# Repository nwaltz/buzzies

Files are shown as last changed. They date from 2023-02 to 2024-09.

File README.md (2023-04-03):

# buzzies
bilateral stimulation tappers for use as a EMDR therapy device through Engineers Without Borders OSU

top level models:

pods: final pod assm.SLDASM

pcb case: pcb assm no snaps.SLDASM

## Production

There are several ways to manufacture the mechanical components needed to house the electrical components for the buzzies.  While the original design concept was produced using a resin SLA printer (Prusa SLIS and Formlabs 3+), components were also designed for injection molding and filament 3D printing.  Each component will have subfolders containing the CAD models, and the subsections below will describe how to manufacture these components.

### Resin SLA Printing

The motivation behind using an SLA printer was to retain the smooth and polished surface finish of an injection molded part while allowing for overhangs and otherwise difficult to manufacture features.  There are four unique parts to manufacture in this design: 4 identical pod halves, a pcb base case, a pcb back cover, and a battery back cover.  

The pod halves are rotationally symmetric about the centerline and will hold a small piezo vibration motor in the center cavity.  Since such motors will generally have small, fragile wires, we recommmend soldering larger (e.g. 16 AWG) wires to the ends of the motor wires.  There is space to house the solder connection within the pods to maintain the strength of the connection. 

Once the motors are soldered and housed within the pods, the pod halves need to be fastened together.  The pod halves will self-align when placed together, and will be fastened with two dowel pins.  There should be two small holes on the side of the pod that the wires exit from.  Insert the dowel pins into these holes to fasten the pods together.  The end of the pin should be flush with the face of the pod.  If the pins seem to be sticking, you may need to lightly tap them with a hammer.

### Injection Molding

### Filament Printing

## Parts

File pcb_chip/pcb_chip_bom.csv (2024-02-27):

Id | Designator | Footprint | Quantity | Comment | JLCPCB Part #?optional? | Column1
1 | U2 | DIP-8_W7.62mm | 1 | IC-8P | C5289485
2 | R6,R5 | R_1206_3216Metric | 2 | rb | C245596
3 | Q1,Q2 | SOT-23 | 2 | TIP41A | C141788
4 | R3,R4 | R_1206_3216Metric | 2 | rm | C237774
5 | C2 | CASE-A-3216 | 1 | 1 uF | C128315
6 | R2 | 805 | 1 | 1k? | C5139712
7 | R1 | R_1206_3216Metric | 1 | 240? | C3017200
10 | C1 | SMD,1.6x3.2mm | 1 | 0.1 uF | C2976899
11 | U1 | SOT-223-3_TabPin2 | 1 | LM317M_SOT-223 | C840113
12 | RV1 |  | 1 | pot | C470307

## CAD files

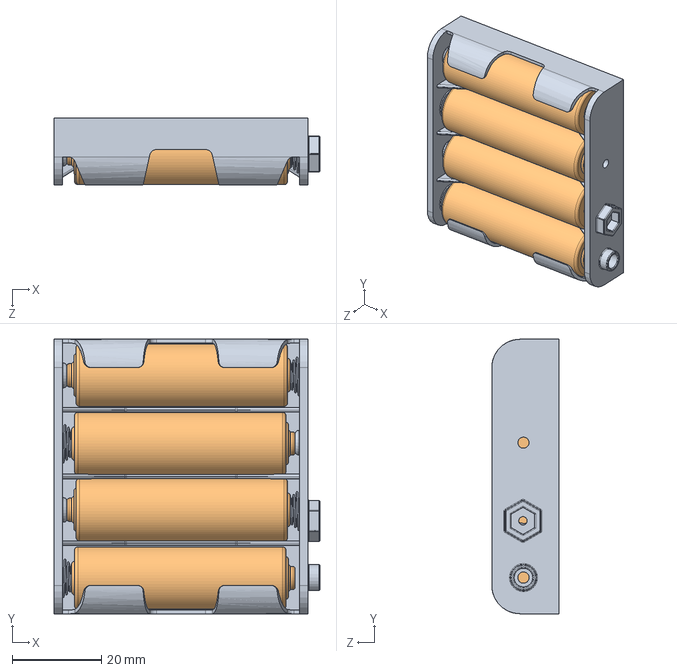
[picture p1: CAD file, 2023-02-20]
pcb assm no snaps/Batterie nel portabatterie.SLDASM
59.6 x 61.5 x 15.1 mm
User Library-R6_AA_UM3-1_5V_holder4AA
Batteria ricaricabile stilo x 4

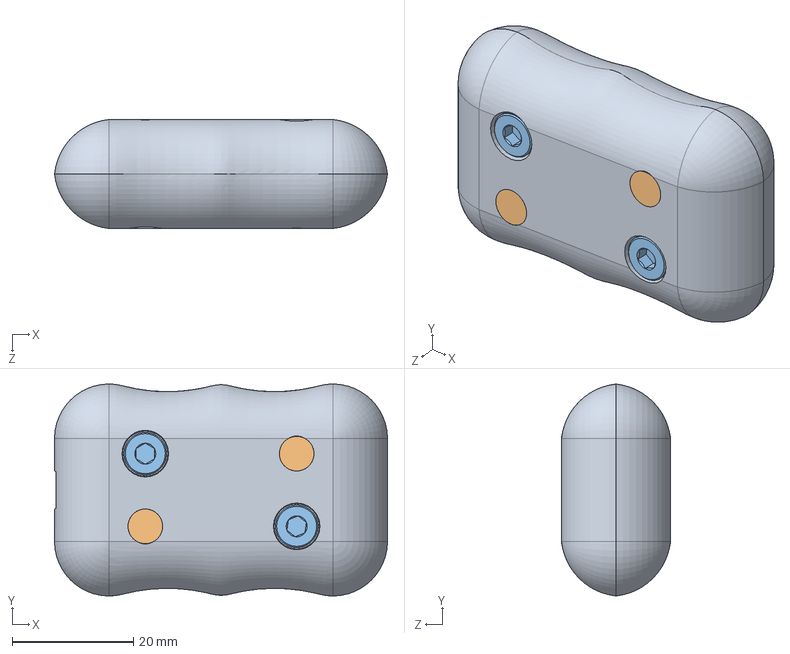
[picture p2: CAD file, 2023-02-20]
final pod assm/final pod assm.SLDASM
55.0 x 35.0 x 18.0 mm
press fit redesign x 2
(INS-PL0008) IBB-M4-4-PennEngineering.stp x 4
91290A148_Alloy Steel Socket Head Screw x 4

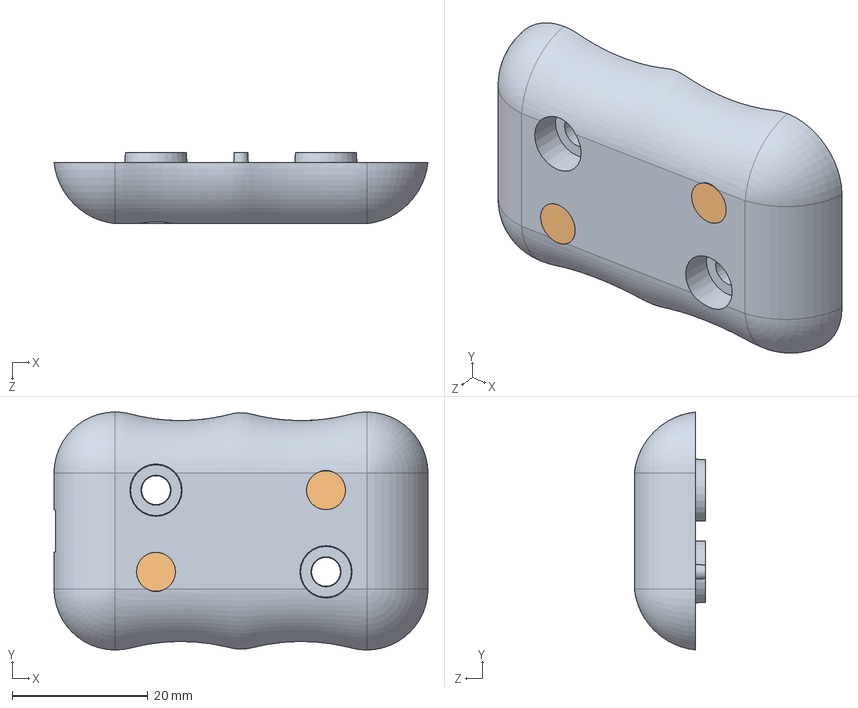
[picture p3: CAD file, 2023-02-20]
final pod assm/press fit assm.SLDASM
55.0 x 35.0 x 10.5 mm
press fit redesign
(INS-PL0008) IBB-M4-4-PennEngineering.stp x 2

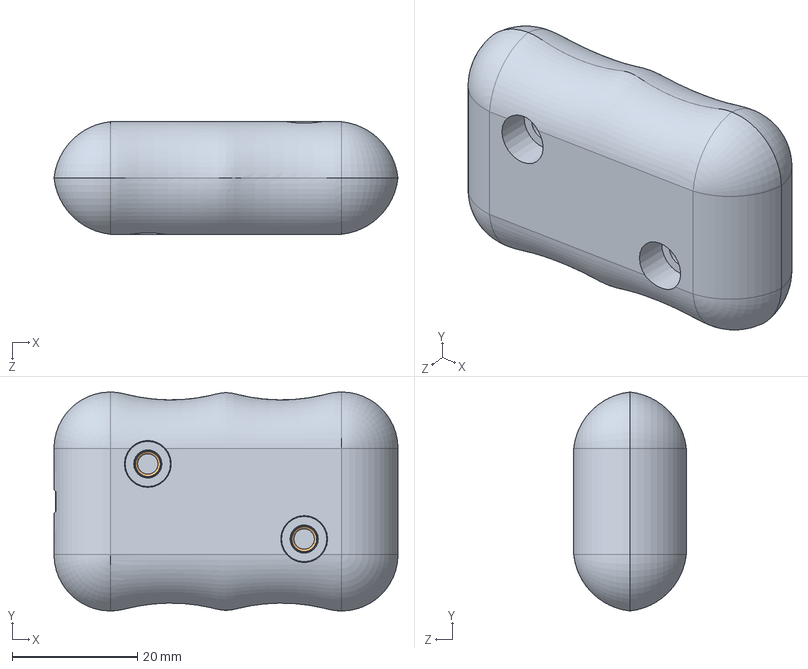
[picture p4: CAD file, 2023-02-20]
final pod assm/pod with inserts test.SLDASM
55.0 x 35.0 x 18.0 mm
snap fit fuck protolabs x 2
(INS-PL0017) STKB-M4-8-PennEngineering.stp x 4

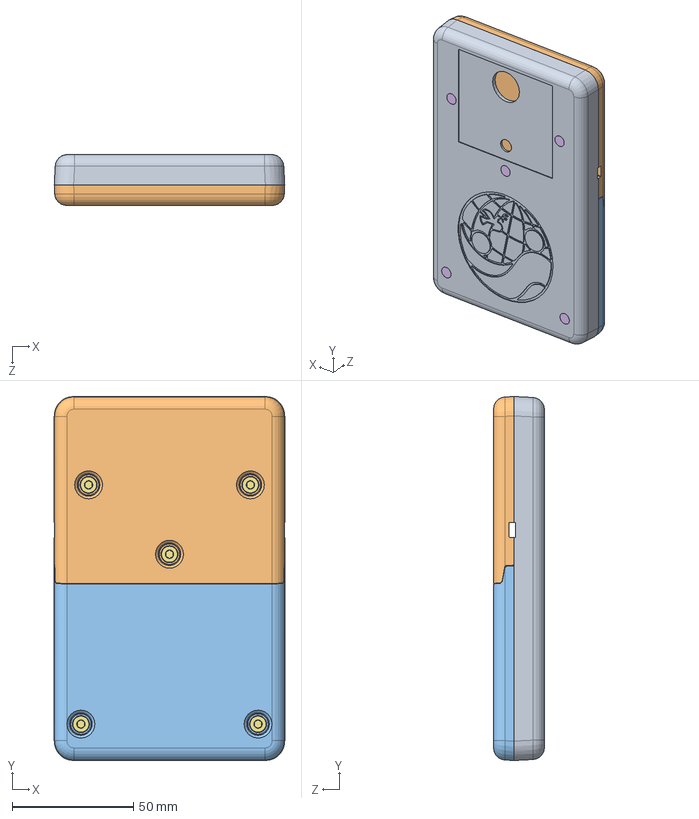
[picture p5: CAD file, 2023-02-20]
pcb assm no snaps/pcb assm no snaps.SLDASM
95.0 x 150.0 x 21.0 mm
pcb top no snaps
pcb bottom no snaps
battery cover no snaps
User Library-R6_AA_UM3-1_5V_holder4AA
Batteria ricaricabile stilo x 4
(INS-PL0008) IBB-M4-4-PennEngineering.stp x 5
91290A148_Alloy Steel Socket Head Screw x 5

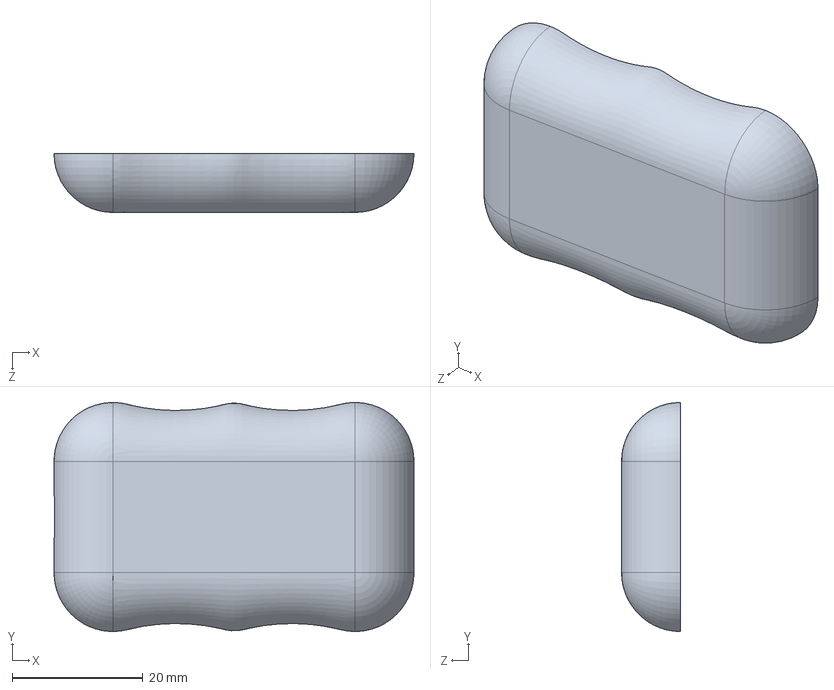
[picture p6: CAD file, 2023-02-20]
final pod assm/pod template.SLDPRT
55.0 x 35.0 x 9.00 mm

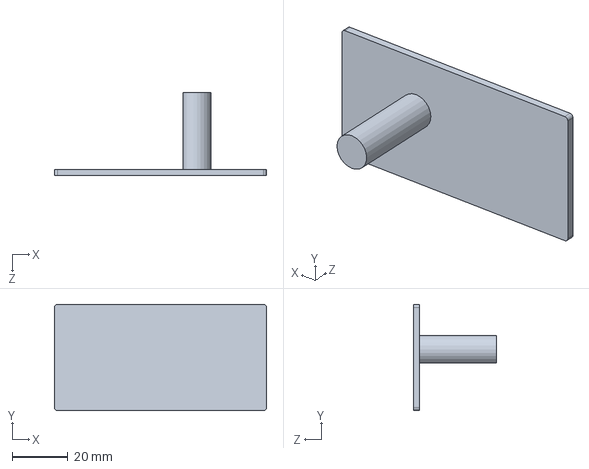
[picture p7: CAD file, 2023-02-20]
pcb assm no snaps/pcb 3x1.5.SLDPRT
76.2 x 38.1 x 30.0 mm

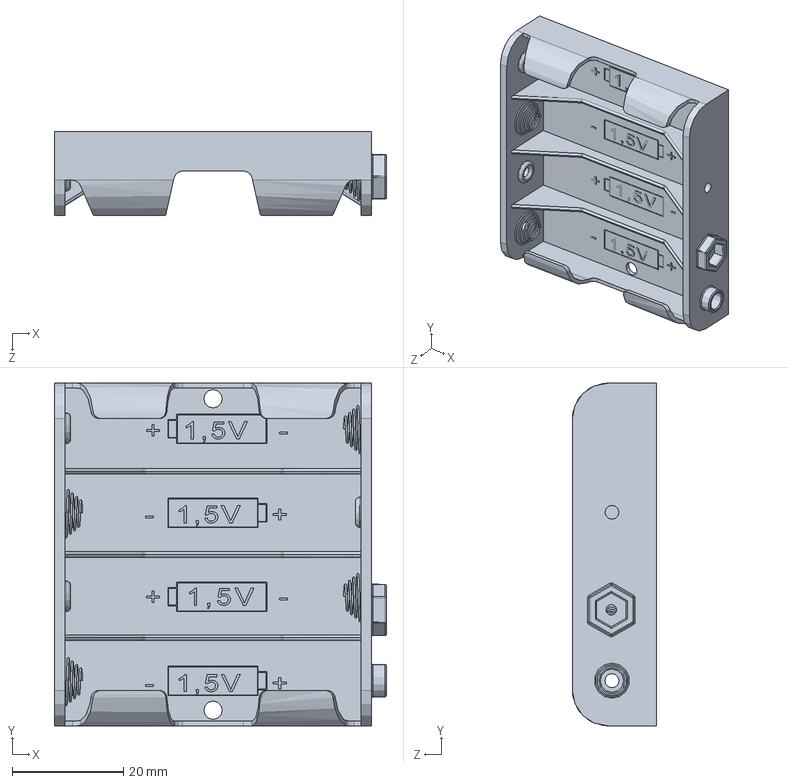
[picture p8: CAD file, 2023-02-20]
pcb assm no snaps/User Library-R6_AA_UM3-1_5V_holder4AA.SLDPRT
59.6 x 61.5 x 15.1 mm

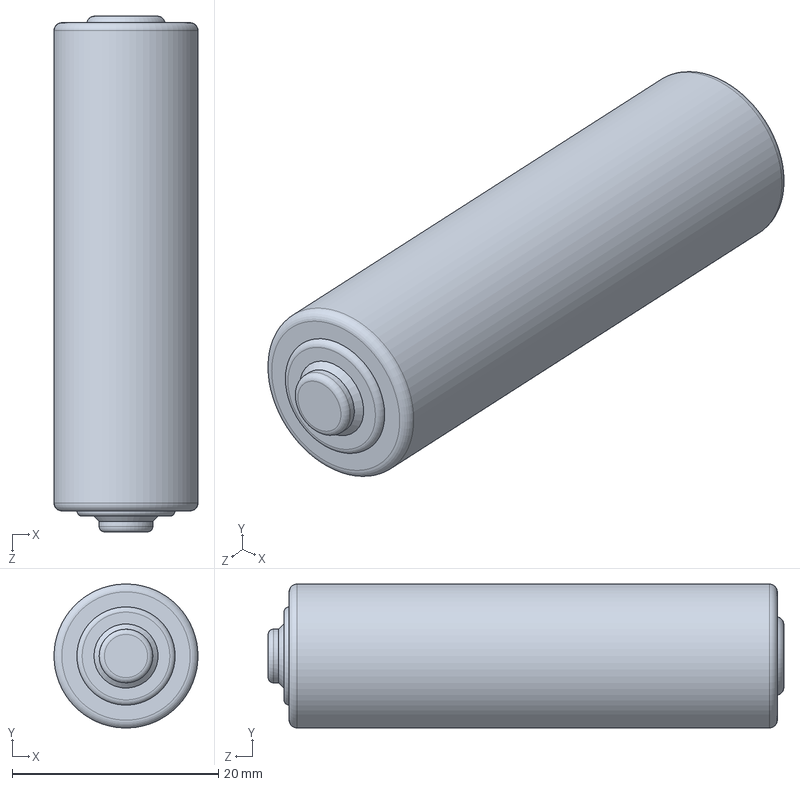
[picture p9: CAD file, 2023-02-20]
pcb assm no snaps/Batteria ricaricabile stilo.SLDPRT
14.0 x 14.0 x 50.0 mm

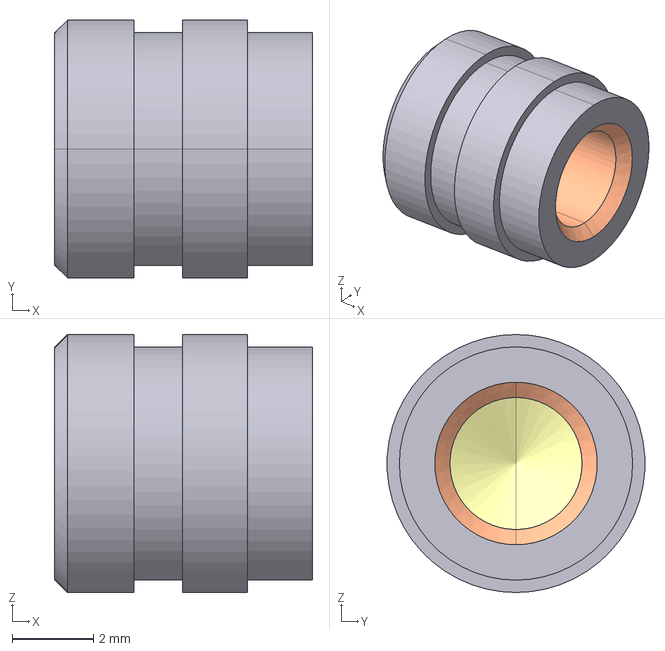
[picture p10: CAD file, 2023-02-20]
final pod assm/(INS-PL0008) IBB-M4-4-PennEngineering.stp
6.35 x 6.34 x 6.35 mm

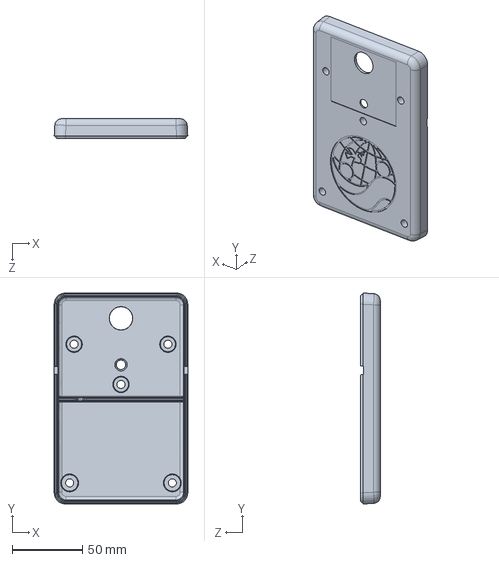
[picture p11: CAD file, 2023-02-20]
pcb assm no snaps/pcb top no snaps.SLDPRT
95.0 x 150.0 x 14.0 mm

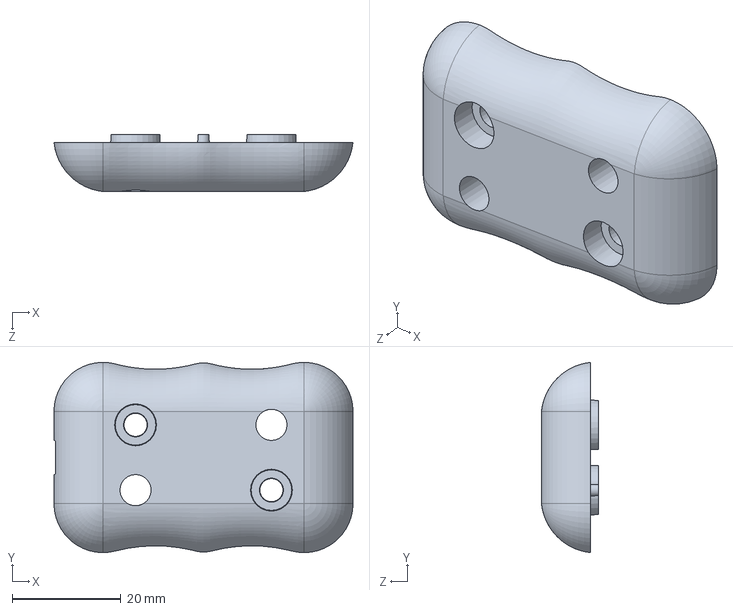
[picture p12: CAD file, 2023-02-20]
final pod assm/press fit redesign.SLDPRT
55.0 x 35.0 x 10.5 mm

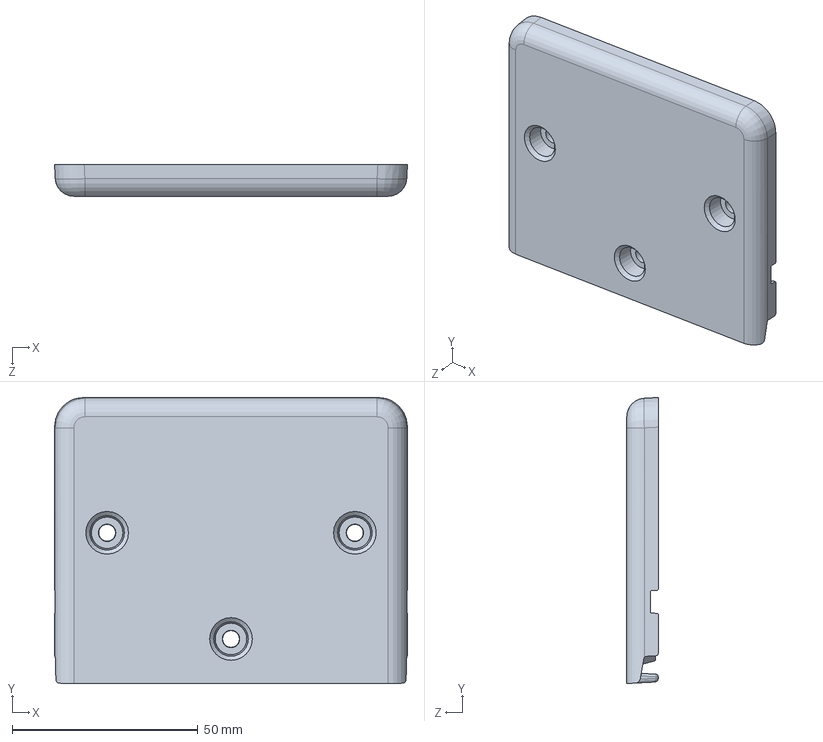
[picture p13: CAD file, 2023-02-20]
pcb assm no snaps/pcb bottom no snaps.SLDPRT
95.0 x 77.0 x 8.50 mm

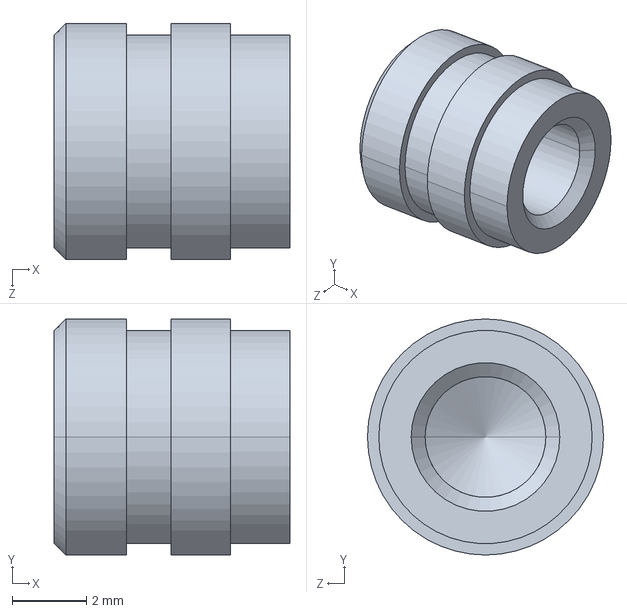
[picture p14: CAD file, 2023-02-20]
final pod assm/(INS-PL0008) IBB-M4-4-PennEngineering.stp.SLDPRT
6.35 x 6.35 x 6.35 mm

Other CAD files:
pcb assm no snaps/battery cover no snaps.SLDPRT
final pod assm/91290A148_Alloy Steel Socket Head Screw.SLDPRT

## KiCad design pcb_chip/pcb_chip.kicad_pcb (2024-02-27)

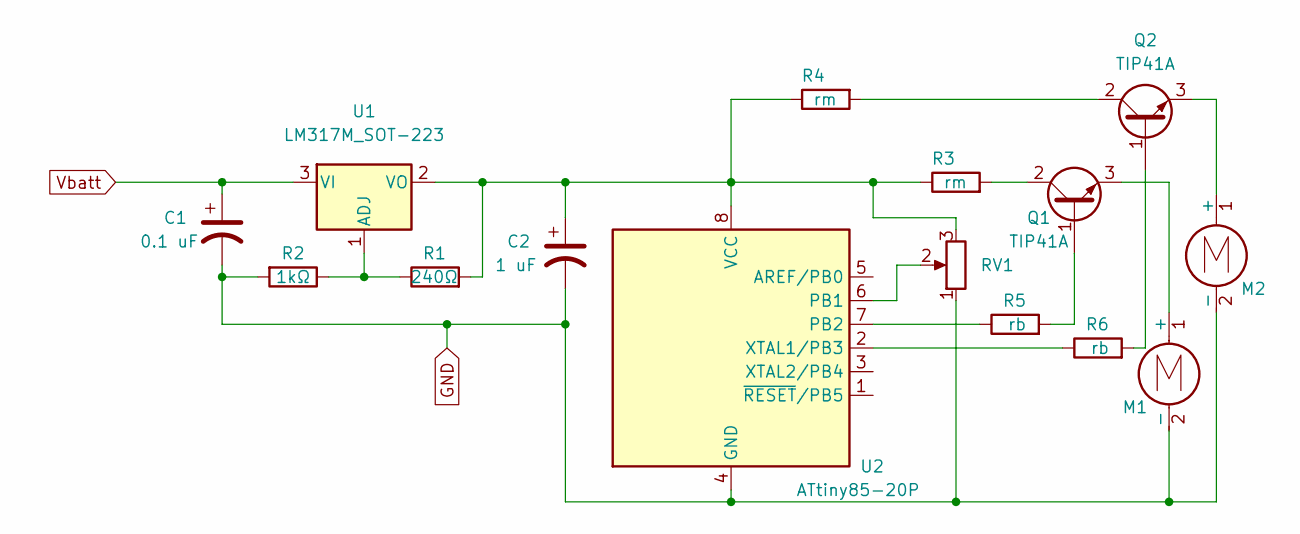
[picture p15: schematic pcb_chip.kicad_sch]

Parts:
C1: 0.1 uF; CP_Elec_4x5.4
C2: 1 uF; CP_Elec_4x5.4
M1, M2: vib_mot; PinHeader_1x02_P2.54mm_Vertical
Q1, Q2: TIP41A; SOT-23
R1: 240Ω; R_1206_3216Metric
R2: 1kΩ; R_1206_3216Metric
R3, R4: rm; R_1206_3216Metric
R5, R6: rb; R_1206_3216Metric
RV1: R_Potentiometer
U1: LM317M_SOT-223; SOT-223-3_TabPin2
U2: ATtiny85-20P; DIP-8_W7.62mm

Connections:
GND: C1.2, C2.2, M1.2 (-), M2.2 (-), R2.2, RV1.1, U2.4 (GND); also elsewhere on the board
unnamed: C2.1, R1.2, R3.1, R4.1, RV1.3, U1.2 (VO), U2.8 (VCC)
unnamed: M1.1 (+), Q1.3 (E)
unnamed: M2.1 (+), Q2.3 (E)
unnamed: R1.1, R2.1, U1.1 (ADJ)
unnamed: Q1.2 (C), R3.2
unnamed: Q2.2 (C), R4.2
unnamed: R5.1, U2.7 (PB2)
unnamed: Q1.1 (B), R5.2
unnamed: R6.1, U2.2 (XTAL1/PB3)
unnamed: Q2.1 (B), R6.2
unnamed: RV1.2, U2.6 (PB1)
Vbatt: C1.1, U1.3 (VI); also elsewhere on the board

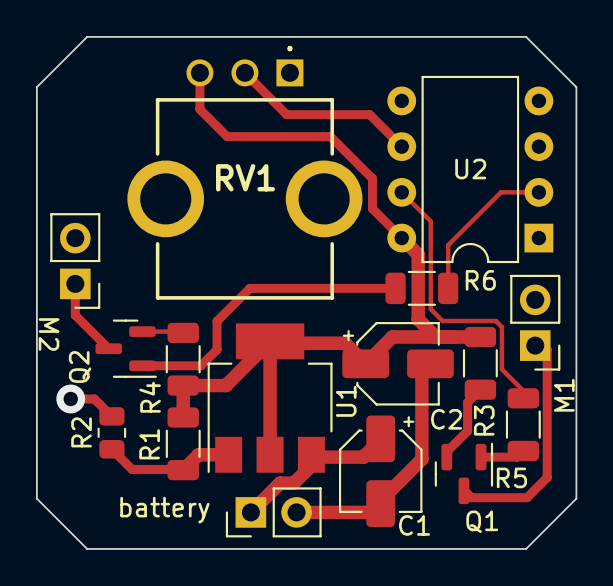
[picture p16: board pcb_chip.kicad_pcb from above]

Board: 2 copper layers, 30.0 x 28.4 mm, 16 parts (0 on the bottom side), 13 nets.

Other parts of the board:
battery: vib_mot; PinHeader_1x02_P2.54mm_Vertical

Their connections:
GND: battery.2 (-); also elsewhere on the board
Vbatt: battery.1 (+); also elsewhere on the board

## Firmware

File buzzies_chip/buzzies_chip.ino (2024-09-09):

int motor_l = 2;
int motor_r = 3;
int pot = 1; // pin 2

int delay_time, analog_in;
int motor_state = 0;
int last_time;

void setup()
{
  pinMode(motor_l, OUTPUT);
  pinMode(motor_r, OUTPUT);
  pinMode(pot, INPUT);
  last_time = millis();
}

void loop()
{
  analog_in = analogRead(pot);
  delay_time = map(analog_in, 0, 1023, 1000, 3000);
  digitalWrite(motor_l, LOW);
  digitalWrite(motor_r, LOW);
  delay(delay_time);
  digitalWrite(motor_l, LOW);
  digitalWrite(motor_r, LOW);
  delay(delay_time);

  
//  if (millis() - last_time > delay_time) {
//    last_time = millis();
//    if (motor_state == 0) {
//      digitalWrite(motor_l, HIGH);
//      digitalWrite(motor_r, LOW);
//      motor_state = 1;
//    }
//    else {
//      digitalWrite(motor_r, HIGH);
//      digitalWrite(motor_l, LOW);
//      motor_state = 0;
//    }
//  }
}

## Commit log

2023-02-20 updated dependencies
    [(INS-PL0008) IBB-M4-4-PennEngineering.stp, (INS-PL0008) IBB-M4-4-PennEngineering.stp.SLDPRT, 91290A148_Alloy Steel Socket Head Screw.SLDPRT, final pod assm.SLD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]
2023-02-20 pod template
    [pod template.SLDPRT]
2024-02-27 added pcb files
    [pcb_chip-B_Cu.gbl, pcb_chip-B_Mask.gbs, pcb_chip-B_Paste.gbp, pcb_chip-B_Silkscreen.gbo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]
2024-08-30 added pod cad file, it does have snaps ignore the name
    [pod no snaps.SLDPRT]
2024-09-29 Rename pod no snaps.SLDPRT to pod with snaps.SLDPRT
    [pod no snaps.SLDPRT, pod with snaps.SLDPRT]
